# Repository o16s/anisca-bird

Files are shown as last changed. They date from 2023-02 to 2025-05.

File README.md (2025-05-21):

# Anisca Bird

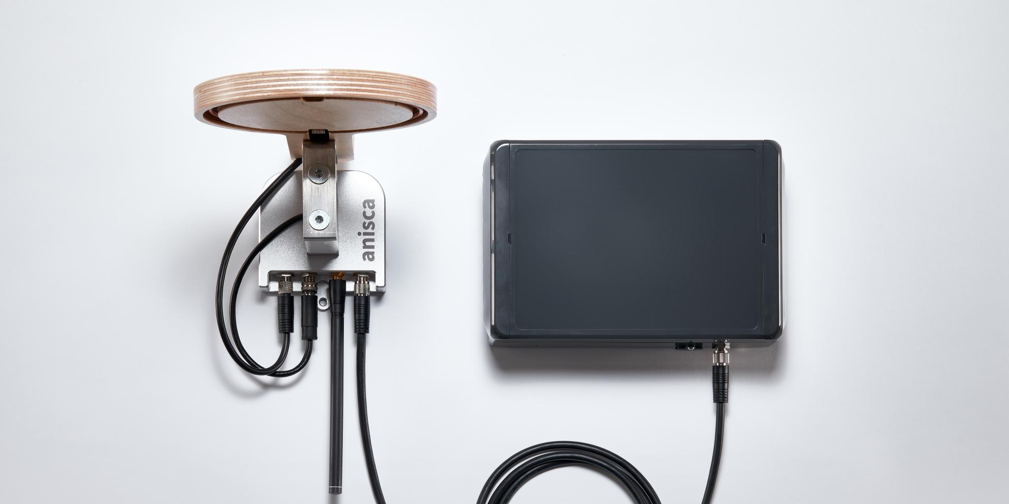
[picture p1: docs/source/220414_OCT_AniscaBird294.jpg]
Anisca Bird


## Overview

Anisca Bird is a smart weighing and tracking device developed by Octanis Instruments in collaboration with the Swiss Ornithological Institute. The system replaces a bird's regular roosting place with a weighing and tracking device that can register a bird's identity and body weight throughout the year without causing stress to the animal.

This repository contains the firmware, PCB design files, and mechanical designs to build and operate the Anisca Bird system.

## Key Features

- **RFID Identification**: Automatically reads passive RFID tags attached to birds
- **Weight Measurement**: Precision load cell with 1g resolution when calibrated
- **Data Storage**: Onboard memory for up to 18 years of weight records
- **Wireless Connectivity**: Optional Sigfox connectivity for remote data transmission
- **USB Connection**: Easy data transfer via USB-C port
- **Long Battery Life**: Up to 1 year with the external battery box
- **Modular Design**: Easy to modify, repair, or upgrade

## Repository Structure

- **`/mechanical`**: Mechanical design files (STEP format)
- **`/nestbox-electronics-master`**: PCB design files for the main board, RFID antenna, and battery box
  - **`/LF_Antenna_v3`**: RFID antenna PCB design
  - **`/Nestbox_v3_3*`**: Main board iterations
  - **`/battery_box`**: Battery box PCB design
  - **`/lib_fp.pretty`**: KiCad footprint libraries
  - **`/lib_sch`**: KiCad schematic libraries
- **`/nestbox-firmware-REV3.3`**: Firmware source code
  - **`/nestbox-fw`**: Core firmware files
  - **`/Core`**: Main application code
  - **`/Drivers`**: Hardware driver files
  - **`/Middlewares`**: Middleware components
  - **`/USB_DEVICE`**: USB communication stack

## Hardware Overview

The Anisca Bird system consists of three main components:

1. **Reader**: Contains the main PCB with microcontroller, load cell interface, RFID reader, flash memory, and connectivity options. Housed in a water-resistant aluminum case.

2. **Perch**: Varnished plywood perch with integrated 125kHz RFID antenna for tag reading with up to 10cm range.

3. **Battery Box**: External battery case with four 10Ah NiMH D-cells providing up to 1 year of operation.

## Firmware Overview

The firmware is built for STM32L433 microcontroller and provides the following functionality:

- RFID tag detection and decoding
- Weight measurement and analysis
- Low-power operation for extended battery life
- USB communication for data retrieval and configuration
- Optional Sigfox connectivity for remote data transmission

## License

Where not otherwise specified, the [GPL License](LICENSE) applies.

## Contact

For commercial support or to request an Anisca Bird system, please contact:

Octanis Instruments GmbH  
Europa-Strasse 33, 8152 Glattbrugg, Switzerland  
info@octanis.ch  
www.octanis.ch

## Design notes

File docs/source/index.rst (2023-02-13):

Welcome to Anisca Bird's documentation!
===================================

Anisca Bird replaces the usual roosting place with a weighing and tracking 
device and can be used with owls, eagles, pigeons, chickens and any other bird that can be ringed.

Contents
--------

.. toctree::
   weight
   status
   webhooks

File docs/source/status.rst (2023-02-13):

Device Status
===================================

While the anisca device is running, ystem status data is continuously logged and stored on the onboard memory ("offline"). Some logs are also transmitted wirelessly via SIGFOX ("uplink" - if coverage is available).

Logging frequency:

* offline: every 3 minutes
* uplink: 3x per day

For more details on the logged data fields see: :ref:`Status <Status Message>`.

Battery Voltage
--------

The battery voltage is measured directly on the mainboard using a resistive divider and an onboard ADC. The reference voltage is VCC, generated from the 3.3V buck converter.

The ADC value is scaled in order to indicate the battery voltage in mV.

Limits and Thresholds
~~~~~~~~~~~~~~~~~~~~~~~~~~~~~~
Rechargeable NiMH batteries should not be discharged below 0.9V per cell. Depending on the measured battery voltage, the device may decide to go to deep-sleep mode in order to protect the batteries.

Below are the hard-coded voltage values that are used to characterize the batteries' charging state. Note that 4x NiMH are powering the system (nominal 4 x 1.2 V)

* VBAT_FULL: 5350 mV. 
  Batteries are considered to be 100% charged
* VBAT_EMPTY: 3600 mV. 
  Batteries are considered to be 0% charged
* VBAT_SHUTDOWN: 3800 mV. When below this voltage, the system will go to deep sleep and weight logging and message transmission is disabled.
* VBAT_STARTUP_MIN: 4200 mV. At boot, the battery voltage must be at least this value in order for the device to complete start-up, else it will go directly to deep sleep. This means, the inserted batteries must be charged to at least this value.

Uptime 
--------
Number of days since last reboot. A reboot happens when the batteries get replaced and upon an unexpected error. If the number of days displayed in the uptime field is smaller than the number of days since the last battery replacement, an unexpected error may have occured. Please service the device if this is observed multiple times. 

Memory usage
--------
The onboard-memory can store up to 3 million log messages. The memory usage is reported as percentage (100 = memory full). The memory can be erased using the anisca App. 

Clock difference
--------
The on-board clock may drift by several seconds per day. If the device has SIGFOX connectivity and the clock difference is too high, a clock update is performed once per day. The clock can also be updated by connecting to the device via USB and using the anisca App.

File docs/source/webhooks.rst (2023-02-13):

Webhooks
===================================

The primary method that Anisca Bird uses to deliver data is through the use of webhooks.
A webhook URL will be called via a POST request with the message encoded as a JSON body. 

Messages
--------

Your webhook URL should be prepared to receive the following messages:

``weight``: Bird detected and weighed
~~~~~~~~~~~~~~~~~~~~~~~~~~~~~~~~~~~~~
.. _Weight Message:

This message is sent when a ringed bird is detected on the perch. A detection is valid if the RFID tag was successful read.

.. http:post:: example.com/webhook

    **Example request body**:

    .. sourcecode:: json

        {
            "timestamp": 1648642396,
            "serial": "CODEABFFEE",
            "device_id": "secret-red-wake",
            "type": "weight",

            "activation": {

                "latlng": "46.535,6.569",
                "site_id": "rdc20",
                "activation_date": 1648641394
            },

            "body": {

                "duration": 12,
                "flags":"ab",
                "weight": 120.5,
                "uid": "0600c9a463",
                "raw_adc_pos": 56020,
                "stddev": 1,
                "temperature": -10
            }
        }

    :<json integer timestamp: Epoch timestamp (UTC+0): seconds since January 1, 1970 12:00:00 AM
    :<json string serial: device serial number
    :<json string device_id: human readable hash of serial number that is also printed on device label
    :<json string type: message type (one of ``weight``, ``status``, ``offset``, or ``calibration``)
    :<json string activation: when and where this device was last activated

    :<json integer duration: number of seconds that owl is on perch (max. 240)
    :<json integer flags: reserved
    :<json integer weight: weight estimate in 0.01 grams (unsigned value)
    :<json integer uid: RFID UID (hexadecimal). Attention: the second byte of the RFID tag is not transmitted in order to save data. Example: The UID 050031b049 will become 0531b049.
    :<json integer raw_adc_pos: raw ADC value from "positive excitation" (incl. offset)
    :<json integer stddev: weight measurement series standard deviation in 0.1 grams
    :<json integer temperature: temperature in degrees Celsius (signed value)

.. _Status Message:
``status``: Device status
~~~~~~~~~~~~~~~~~~~~~~~~~~

Device status is sent twice a day.

.. http:post:: example.com/webhook

    **Example request body**:

    .. sourcecode:: json

        {
            "timestamp": 1648642396,
            "serial": "CODEABFFEE",
            "device_id": "secret-red-wake",
            "type": "status",

            "activation": {

                "latlng": "46.535,6.569",
                "site_id": "rdc20",
                "activation_date": 1648641394
            },

            "body": {

                "header": "ff",
                "events_with_id": 29,
                "events_unknown_id": 16,
                "flags": "ab",
                "vbat_mv": 4620,
                "memory_used": 56,
                "days_since_boot": 120
            }
        }

    :<json integer timestamp: Epoch timestamp (UTC+0): seconds since January 1, 1970 12:00:00 AM
    :<json string serial: device serial number
    :<json string device_id: human readable hash of serial number that is also printed on device label
    :<json string type: message type (one of ``weight``, ``status``, ``offset``, or ``calibration``)
    :<json string activation: when and where this device was last activated

    :<json integer header: internal device status header (0xFF)
    :<json integer events_with_id: number of events with successful RFID detection since last status update [0-255]. The value of 255 means >=255.
    :<json integer events_unknown_id: number of events with UN-successful RFID detection since last status update [0-255]. The value of 255 means >=255.
    :<json integer flags: reserved
    :<json integer vbat_mv: Battery voltage in mV
    :<json integer memory_used: Percentage of Flash memory used [0-100]
    :<json integer days_since_boot: Number of days since last reboot [0-255]. The value of 255 means >=255.

``offset``: Tare weight
~~~~~~~~~~~~~~~~~~~~~~~~~~

This is the tare weight (unladen weight) and is sent every 2 hours.

.. http:post:: example.com/webhook

    **Example request body**:

    .. sourcecode:: json

        {
            "timestamp": 1648642396,
            "serial": "CODEABFFEE",
            "device_id": "secret-red-wake",
            "type": "offset",
            
            "activation": {

                "latlng": "46.535,6.569",
                "site_id": "rdc20",
                "activation_date": 1648641376
            },

            "body": {

                "header": "fa",
                "flags": "ac",
                "weight": 31660,
                "raw_adc_pos": 4999,
                "raw_adc_neg": 4986,
                "stddev": 0,
                "temperature": 20
            }
        }

    :<json integer timestamp: Epoch timestamp (UTC+0): seconds since January 1, 1970 12:00:00 AM
    :<json string serial: device serial number
    :<json string device_id: human readable hash of serial number that is also printed on device label
    :<json string type: message type (one of ``weight``, ``status``, ``offset``, or ``calibration``)
    :<json string activation: when and where this device was last activated

    :<json integer header: internal device status header (0xFA)
    :<json integer flags: reserved
    :<json integer raw_adc_pos: raw tare ADC value from "positive excitation"
    :<json integer raw_adc_neg: raw tare ADC value from "negative excitation"
    :<json integer stddev: tare measurement series standard deviation in 0.1 grams
    :<json integer temperature: temperature in degrees Celsius (signed value)

``calibration``: Calibration result
~~~~~~~~~~~~~~~~~~~~~~~~~~~~~~~~~~~~~~~~~~

This message is sent after the user has performed a calibration.

.. http:post:: example.com/webhook

    **Example request body**:

    .. sourcecode:: json

        {
            "timestamp": 1648642396,
            "serial": "CODEABFFEE",
            "device_id": "secret-red-wake",
            "type": "calibration",

            "activation": {

                "latlng": "46.535,6.569",
                "site_id": "rdc20",
                "activation_date": 1648641376
            },

            "body": {

                "slope": 29,
                "intercept": 25,
                "temperature": 2,
                "r2": 1.0
            }
        }

    :<json integer timestamp: Epoch timestamp (UTC+0): seconds since January 1, 1970 12:00:00 AM
    :<json string serial: device serial number
    :<json string device_id: human readable hash of serial number that is also printed on device label
    :<json string type: message type (one of ``weight``, ``status``, ``offset``, or ``calibration``)
    :<json string activation: when and where this device was last activated

    :<json integer slope: linear regression slope: (raw ADC counts per 10mg)
    :<json integer intercept: linear regression intercept: (raw ADC value)
    :<json float r2: linear regression R^2
    :<json integer temperature: temperature in degrees Celsius (signed value)

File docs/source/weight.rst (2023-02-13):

Weight Measurement
===================================

Any bird weighing event is recorded and stored to memory as a new log entry. In addition, continuous offset measurements and calibration data are logged. The most important logs are also transmitted wirelessly via SIGFOX (if coverage is available).

Bird Weight
--------
Anisca Bird continuously measures the weigth present on the wooden perch ("Detection"). It does so in a low-power fashion until the measured weight is above WAKE_UP_THRESHOLD. The device then attempts to read the RFID tag of a potential bird present. If successful, the weight is measured continuously ("Acquisition") for as long as it stays above WAKE_UP_THRESHOLD.

Detection
~~~~~~~~~~~~~~~~~~~~~~~~~~~~~~

During detection, the following hard-coded constants are used:

* Low-power detection interval: 1 second
* WAKE_UP_THRESHOLD: 50 grams [#f1]_
* RFID read attempts: max. 10x in 3 second intervals. If unsuccessful after this, system goes back to sleep.

Acquisition
~~~~~~~~~~~~~~~~~~~~~~~~~~~~~~
After a bird was detected and a valid RFID was read out, its weight is sampled continuously. Multiple samples are taken into account 
because the bird may be moving and hence an instantaneous measurement would not provide a reliable weight value. 

The final **raw weight** value is obtained as a result of 3 acquisition steps:

1. **Sub-samples**: The load cell ADC is sampling the weight at 10 Hz. 
2. **Samples**: Always 10 sub-samples are averaged to create one sample. A standard deviation on the 10 sub-samples is calculated. 

    a. If the sub-sample standard deviation for a given group of 10 exceeds MAX_SUB_STDEV, the sample gets discarded. This ensures only samples where the bird was sitting still will be considered.
    b. If a sample is MAX_SAMPLE_DIFF larger than the previous sample, then the previous sample gets discarded. This ensures all samples to be on a relatifely flat line and removes outliers.

3. **Median**: A maximum of N_SAMPLES is collected as described in points 1 & 2. If the bird leaves before reaching N_SAMPLES, a smaller number of samples will be available.

    a. The median value over all collected samples is calculated. This is the retained **raw weight** value.
    b. The standard deviation over all collected samples is calculated. This is the retained **raw stddev** value.

Hard-coded parameters:

* MAX_SUB_STDEV: 5 grams [#f1]_
* MAX_SAMPLE_DIFF: 5 grams [#f1]_
* N_SAMPLES: 19

Processing
~~~~~~~~~~~~~~~~~~~~~~~~~~~~~~
The **raw weight** and **raw stddev** values obtained above are unitless ADC values. They need to be converted to grams using calibration data in order to present meaningful weight data. This is done as follows:

1. The last recorded **raw offset** value is subtracted from the **raw weight**, in order to receive the **net raw weight**
2. **net raw weight** and  **raw stddev** are divided by the most recently measured **calibration slope** to obtain weight and standard deviation of the sample in grams.

Logging
~~~~~~~~~~~~~~~~~~~~~~~~~~~~~~
For more details on what data is logged or transmitted, see: :ref:`Weight <Weight Message>`.

Offset measurement
--------

The **raw offset** is measured in the exact same way as the bird weight, except that it happens in a periodic manner whenever the weight detection stays below the WAKE_UP_THRESHOLD. 

The following parameters are hard-coded:

* N_OFFSET_SAMPLES: 11
* Offset acquisition & logging period: 3 minutes
* Offset uplink period (transmitted via SIGFOX): 1-2 hours

Calibration 
--------

The calibration is a linear regression between raw ADC values and the weight placed on the perch in grams. We denote the following terms:

* **Slope (a)**: the multiplication factor between grams and raw ADC value
* **Intercept (b)** the calculated raw ADC value when zero weight is placed on the perch. Theoretically, this is the offset value during calibration.
* **R^2** the R-square of the linear regression.

When performing a calibration routine, both a and b are calculated automatically by the device and stored for internal use. All subsequent weight measurements are processed using these most up-to-date calibraion values.

It is known that the calibration values can change over time as the physical state of the sytstem changes. Therefore, frequent re-calibrations of the system are advised.

Temperature Dependency
~~~~~~~~~~~~~~~~~~~~~~~~~~~~~~

It is known that notably the calibration slope is temperature dependent. This dependency is not compensated for by the device. It is adviseed to perform a temperature compensation of the logged weight values once the relationship between temperature and slope has been established in a post-processing step. 

.. rubric:: Footnotes
.. [#f1] Note: the values in grams are internally converted into raw ADC values by using the last available calibration slope.

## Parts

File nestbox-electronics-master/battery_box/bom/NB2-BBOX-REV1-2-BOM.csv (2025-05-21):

Reference | Quantity | Value | Footprint | Datasheet | MPN | MPN2
BT1 | 1 | Battery-4xNiMH | TerminalBlock_Dinkle:TerminalBlock_Dinkle_DT-55-B01X-02_P10.00mm
BZ1 | 1 | DNP | Buzzer_Beeper:Buzzer_CUI_CPT-9019S-SMT |  | SMT-0827-SW-5V-R
C1 C2 C3 | 3 | 10u | Capacitor_SMD:C_0805_2012Metric
C101 | 1 | DNP | Capacitor_SMD:C_0805_2012Metric
D1 | 1 | DNP | Diode_SMD:D_SOD-323 |  | B0520WS-7-F
D2 | 1 | schottky | Diode_SMD:D_SOD-323 |  | B0520WS-7-F
D3 | 1 | Red LED | LED_THT:LED_D5.0mm |  | WP934EW/ID
D4 | 1 | DNP | Package_TO_SOT_SMD:SOT-723 |  | SZESD7205DT5G
D5 | 1 | TVS DIODE 12V 23.7V | Diode_SMD:D_SOD-523 |  | UCLAMP1201H.TCT
G1 | 1 | LOGO | lib_fp_global:oi_logo_small
H1 H3 H5 H7 | 4 | MountingHole_Pad | MountingHole:MountingHole_4.5mm
H2 H4 H6 H8 | 4 | MountingHole_Pad | MountingHole:MountingHole_3.5mm
J1 J3 | 2 | FC-M8-5 | lib_fp:M8-5 | http://www.mouser.com/ds/2/18/40_c091_abd_e-75918.pdf | MB08MBSBFF05RA | 1424240
J2 | 1 | USB_C_Receptacle_USB2.0 | lib_fp:USB_C_Receptacle_HRO_TYPE-C-31-M-12 | https://www.jae.com/en/releases/detail/id=92529 | USB4105-GF-A
LOGO1 | 1 | Logo_Open_Hardware_Small | lib_fp:VogelwarteLogo3
LS1 | 1 | SMT-0931-S-R | lib_fp:SMT-0931-S-R |  | SMT-0931-S-R
Q1 | 1 | NMOS 30V 4A | Package_TO_SOT_SMD:SOT-23 |  | PMV45EN2R
Q2 | 1 | PMOS 20V 3A | Package_TO_SOT_SMD:SOT-23 |  | DMP2160U-7
R1 | 1 | 1k | Resistor_SMD:R_0603_1608Metric
R2 | 1 | 430R | Resistor_SMD:R_0603_1608Metric
R3 R5 | 2 | 0R | Resistor_SMD:R_0603_1608Metric
R4 R6 R7 R8 | 4 | 5k1 | Resistor_SMD:R_0603_1608Metric
R10 R101 R9 | 3 | DNP | Resistor_SMD:R_0603_1608Metric

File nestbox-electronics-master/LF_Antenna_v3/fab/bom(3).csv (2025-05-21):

Row | Description | Part | References | Value | Footprint | Quantity Per PCB | Datasheet | MPN
1 |  | CONSMA003.031-G | J1 | SMA-Female | LINX_CONSMA003.031-G | 1 |  | CONSMA003.031
2 | Inductor | L | L1 | LF-ANT | R_1206_3216Metric | 1 | ~ | OCTANIS-JZCOIL-120
Project info:
Schematic: | LF_Antenna_v3
Variant: | default
Revision:
Date: | 2021-03-15_15-58-28
KiCad Version: | 5.1.6-c6e7f7d~87~ubuntu20.04.1
Statistics:
Component Groups: | 2
Component Count: | 2
Fitted Components: | 2
Number of PCBs: | 1
Total Components: | 2

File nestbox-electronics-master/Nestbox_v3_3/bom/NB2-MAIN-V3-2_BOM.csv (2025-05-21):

Reference | Quantity | Value | Footprint | Datasheet | MPN | MPN2 | Description | Height | MPN-adj
BT1 | 1 | Battery-RESCUE-Nestbox_v1 | Battery:BatteryHolder_MPD_BC2003_1x2032 |  | BAT-HLD-002-SMT
C101 C201 C203 C208 C209 C210 C401 C501 C503 | 9 | 10u | Capacitor_SMD:C_0805_2012Metric
C205 | 1 | 330p | Capacitor_SMD:C_0603_1608Metric
C207 | 1 | 33p | Capacitor_SMD:C_0603_1608Metric
C206 C301 C302 | 3 | 12p | Capacitor_SMD:C_0603_1608Metric
C303 C304 | 2 | 22p | Capacitor_SMD:C_0603_1608Metric
C202 C204 C305 C311 C312 C608 | 6 | 1u | Capacitor_SMD:C_0603_1608Metric
C306 C307 C308 C313 C502 C504 C507 C508 C606 C609 C611 | 11 | 100n | Capacitor_SMD:C_0603_1608Metric
C310 C505 C506 C509 | 4 | 10n | Capacitor_SMD:C_0603_1608Metric
CRES502 CRES503 | 2 | 1n5 450V C0G | Capacitor_SMD:C_0805_2012Metric |  | CGA4F4C0G2W152J085AE
Cdiv501 | 1 | 10p 500V | Capacitor_SMD:C_0805_2012Metric |  | C0805C100JDGACTU
Cdiv502 | 1 | 1n | Capacitor_SMD:C_0603_1608Metric
D101 D302 | 2 | ESD7205 | Package_TO_SOT_SMD:SOT-723 |  | SZESD7205DT5G
D201 | 1 | TVS DIODE 12V 23.7V | Diode_SMD:D_0402_1005Metric |  | ESD9X12ST5G
D303 | 1 | LED_YELLOW | LED_SMD:LED_0603_1608Metric
J101 | 1 | FC-M8-5 | lib_fp:M8-5 | http://www.mouser.com/ds/2/18/40_c091_abd_e-75918.pdf | MB08MBSBFF05RA | 1424240
J401 J402 | 2 | Conn_01x10_Female | Connector_PinSocket_2.00mm:PinSocket_1x10_P2.00mm_Vertical_SMD_Pin1Right |  | NPPN101BFLC-RC
J1 J601 | 2 | LOAD_CELL_CONN_01X04 | lib_fp:MB08MBSAFF04RA |  | MB08MBSAFF04RA | M8S-04PMMR-SF8001
L201 | 1 | 5uH | Inductor_SMD:L_Taiyo-Yuden_NR-60xx_HandSoldering |  | MSS7341-502NLD
L202 | 1 | 4.7uH | Inductor_SMD:L_1008_2520Metric |  | DFE252010P-4R7M=P2
L301 | 1 | 10u | Inductor_SMD:L_0402_1005Metric |  | MPZ1005S300CT000
Q201 | 1 | TPH1R712MDL1Q | lib_fp:TDSON-8-1_HandSoldering |  | TPH1R712MD,L1Q
Q301 Q601 Q603 | 3 | PMOS 20V 3A | Package_TO_SOT_SMD:SOT-23 |  | DMP2160U-7
Q501 Q602 Q604 | 3 | NMOS 30V 4A | Package_TO_SOT_SMD:SOT-23 |  | PMV45EN2R
R101 R102 R303 R307 R605 R615 R616 R617 | 8 | 47R | Resistor_SMD:R_0603_1608Metric
R202 R203 R207 | 3 | 162k 0.1% | Resistor_SMD:R_0603_1608Metric
R206 | 1 | 15k | Resistor_SMD:R_0603_1608Metric
R208 | 1 | 649k 1% | Resistor_SMD:R_0603_1608Metric
R306 | 1 | 1k | Resistor_SMD:R_0603_1608Metric
R205 R401 | 2 | 10k | Resistor_SMD:R_0603_1608Metric
R201 R302 R304 R403 R504 R601 R602 R603 R604 | 9 | 100k | Resistor_SMD:R_0603_1608Metric
R501 R607 R608 R611 R612 R614 R618 CRES501 | 8 | 0R | Resistor_SMD:R_0603_1608Metric
U201 | 1 | TPS62745 | lib_fp:WSON_3x2mm_12pin |  | TPS62745DSSR
U202 | 1 | LTC3534 | Package_SO:SSOP-16_3.9x4.9mm_P0.635mm |  | LTC3534EGN#PBF
U203 | 1 | 3.0V LDO | Package_TO_SOT_SMD:SOT-23-5 |  | TPS70630DBVR | TPS7A20 |  |  | TPS76201QDBVRQ1
U301 | 1 | STM32L433CCxx | Package_DFN_QFN:QFN-48-1EP_7x7mm_P0.5mm_EP5.3x5.3mm | http://www.st.com/st-web-ui/static/active/en/resource/technical/document/datasheet/DM00257192.pdf | STM32L433CCU6
U302 | 1 | 1Gb NAND Flash | lib_fp:8-LGA-6x8mm |  | GD5F1GQ4UFYIGR
U401 | 1 | Power Switch 2A, 800us soft start | lib_fp:IC_MIC94085YFT-TR |  | MIC94082YFT-TR
U501 | 1 | EM4095 | Package_SO:SOIC-16_3.9x9.9mm_P1.27mm |  | EM4095
U601 | 1 | ADS1220 | Package_SO:TSSOP-16_4.4x5mm_P0.65mm |  | ADS1220IPW
U602 | 1 | DNP | Oscillator:Oscillator_SMD_EuroQuartz_XO32-4Pin_3.2x2.5mm | https://abracon.com/Oscillators/ASDMB.pdf | SIT1602BI-21-XXS-4.096000
Y301 | 1 | 16MHz 10ppm 9pF | lib_fp:Crystal_SMD_2016-4Pin_2.0x1.6mm |  | ECS-160-9-37-CKM-TR |  | 16MHz ±10ppm Crystal 9pF 100 Ohms 4-SMD, No Lead | 0.6
Y302 | 1 | 32kHz 20ppm 12.5pF | lib_fp:Crystal_SMD_MicroCrystal_CC7V-T1A-2Pin_3.2x1.5mm |  | CM7V-T1A-32.768kHz-12.5pF-20PPM-TB-QC

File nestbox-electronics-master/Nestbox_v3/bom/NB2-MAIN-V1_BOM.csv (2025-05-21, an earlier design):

Reference | Quantity | Value | Footprint | Datasheet | MPN | MPN-adj | MPN2 | Description | Height
C101 C201 C203 C208 C209 C210 C401 C501 C503 C610 | 10 | 10u | Capacitor_SMD:C_0805_2012Metric
C202 C311 C312 C608 | 4 | 1u | Capacitor_SMD:C_0603_1608Metric
C204 | 1 | 1u or 4u7 for adjustable version | Capacitor_SMD:C_0603_1608Metric
C205 | 1 | 330p | Capacitor_SMD:C_0603_1608Metric
C206 | 1 | 10p | Capacitor_SMD:C_0603_1608Metric
C207 | 1 | 33p | Capacitor_SMD:C_0603_1608Metric
C301 C302 | 2 | 12p | Capacitor_SMD:C_0603_1608Metric | ~
C303 C304 | 2 | 22p | Capacitor_SMD:C_0603_1608Metric | ~
C305 | 1 | 4u7 | Capacitor_SMD:C_0603_1608Metric | ~
C306 C307 C308 C313 C502 C504 C507 C606 C609 | 9 | 100n | Capacitor_SMD:C_0603_1608Metric | ~
C310 C505 C506 C611 | 4 | 10n | Capacitor_SMD:C_0603_1608Metric | ~
C508 | 1 | DNP or 100n | Capacitor_SMD:C_0603_1608Metric | DNP
C602 | 1 | 1u DNP | Capacitor_SMD:C_0603_1608Metric
C601 C603 C604 | 3 | 100n 1% DNP | Capacitor_SMD:C_0603_1608Metric
C605 C607 | 2 | 100n DNP | Capacitor_SMD:C_0603_1608Metric
CRES501 | 1 | 0R | Capacitor_SMD:C_0603_1608Metric
CRES502 CRES503 | 2 | 1n5 450V C0G | Capacitor_SMD:C_0805_2012Metric |  | CGA4F4C0G2W152J085AE
Cdiv501 | 1 | 10p 500V | Capacitor_SMD:C_0805_2012Metric |  | C0805C100JDGACTU
Cdiv502 | 1 | 1n | Capacitor_SMD:C_0603_1608Metric
D101 D302 | 2 | ESD7205 | Package_TO_SOT_SMD:SOT-723 |  | SZESD7205DT5G
D301 | 1 | TVS DIODE 12V 23.7V | Diode_SMD:D_0402_1005Metric | ~ | ESD9X12ST5G
D303 | 1 | LED_YELLOW | LED_SMD:LED_0603_1608Metric
G101 | 1 | LOGO | lib-fp-global:oi_logo_small
H101 H102 H103 | 3 | MountingHole_Pad | MountingHole:MountingHole_3.2mm_M3_Pad_Via | ~
J101 | 1 | FC-M8-5 | Connector_Molex:Molex_PicoBlade_53398-0571_1x05-1MP_P1.25mm_Vertical | http://www.mouser.com/ds/2/18/40_c091_abd_e-75918.pdf | 53398-0571
J102 | 1 | Chassis Pin | lib_fp:SMD_PAD | ~
J301 | 1 | USB_B_Micro | Connector_USB:USB_Micro-B_Molex-105017-0001 | ~
J401 J402 | 2 | Conn_01x10_Female | Connector_PinSocket_2.00mm:PinSocket_1x10_P2.00mm_Vertical_SMD_Pin1Left | ~ | 1-2307813-0
J501 | 1 | Conn_RFID_UFL_ALT | Connector_Coaxial:U.FL_Hirose_U.FL-R-SMT-1_Vertical | ~ | U.FL-R-SMT(10)
J502 | 1 | Conn_RFID_SMA | lib_fp:SMA_Molex_EdgeMount | ~ | 0732512120
J601 | 1 | LOAD_CELL_CONN_01X04 | lib_fp:MB08MBSAFF04RA |  | M8S-04PMMR-SF8001 |  | MB08MBSAFF04RA
J602 | 1 | LOAD_CELL_CONN_01X04 | Connector_Molex:Molex_PicoBlade_53398-0471_1x04-1MP_P1.25mm_Vertical |  | 53398-0471
JP201 | 1 | Jumper_3_Bridged12 | Connector_PinHeader_2.54mm:PinHeader_1x03_P2.54mm_Vertical | ~
JP202 | 1 | 5V boost supply jumper | Connector_PinHeader_2.54mm:PinHeader_1x02_P2.54mm_Vertical | ~
JP203 | 1 | vsel 0.2 | Jumper:SolderJumper-3_P1.3mm_Bridged12_RoundedPad1.0x1.5mm | ~
JP204 | 1 | VAA jumper | Connector_PinHeader_2.54mm:PinHeader_1x02_P2.54mm_Vertical | ~
JP205 | 1 | vsel 0.1 | Jumper:SolderJumper-3_P1.3mm_Bridged12_RoundedPad1.0x1.5mm | ~
JP206 JP301 | 2 | Jumper_NC_Small | Connector_PinHeader_2.54mm:PinHeader_1x02_P2.54mm_Vertical | ~
L201 | 1 | 5uH | Inductor_SMD:L_Taiyo-Yuden_NR-60xx_HandSoldering |  | MSS7341-502NLD
L202 | 1 | 4.7uH | Inductor_SMD:L_1008_2520Metric |  | DFE252010P-4R7M=P2
L301 | 1 | 10u | Inductor_SMD:L_0402_1005Metric | ~ | MPZ1005S300CT000
LOGO101 | 1 | Logo_Open_Hardware_Small | lib_fp:VogelwarteLogo3 | ~
P301 | 1 | TC2030-MCP | lib-fp-global:TC2030-MCP-NL
Q201 | 1 | TPH1R712MDL1Q | lib_fp:TDSON-8-1_HandSoldering |  | TPH1R712MD,L1Q
Q301 Q601 Q603 | 3 | DMG2301L-7 | Package_TO_SOT_SMD:SOT-23 |  | DMG2301L-7
Q501 Q602 Q604 | 3 | NMOS 30V 4A | Package_TO_SOT_SMD:SOT-23 |  | SI2316DS-T1-E3
R101 R102 R103 R104 R205 R401 R403 | 7 | 10k | Resistor_SMD:R_0603_1608Metric | ~
R105 R106 R204 R209 R210 R301 R402 R404 R405 R503 R505 R506 R509 R613 R614 | 15 | DNP | Resistor_SMD:R_0603_1608Metric | ~
R201 R202 R302 R304 R504 R601 R602 R603 R604 | 9 | 82k | Resistor_SMD:R_0603_1608Metric
R203 | 1 | 47k | Resistor_SMD:R_0603_1608Metric
R206 | 1 | 15k | Resistor_SMD:R_0603_1608Metric
R207 | 1 | 162k 1% | Resistor_SMD:R_0603_1608Metric |  | RC0402FR-07162KL
R208 | 1 | 649k 1% | Resistor_SMD:R_0603_1608Metric |  | RC0402FR-07649KL
R303 | 1 | 100R | Resistor_SMD:R_0603_1608Metric | ~
R305 | 1 | 1k5 | Resistor_SMD:R_0603_1608Metric | ~
R306 | 1 | 1k | Resistor_SMD:R_0603_1608Metric
R501 R502 R507 R508 R605 R606 R607 R608 R609 R610 R611 R612 R618 | 13 | 0R | Resistor_SMD:R_0603_1608Metric
R615 R616 R617 | 3 | 47R | Resistor_SMD:R_0603_1608Metric
U201 | 1 | TPS62745 | lib_fp:WSON_3x2mm_12pin |  | TPS62745DSSR
U202 | 1 | LTC3534 | Package_SO:SSOP-16_3.9x4.9mm_P0.635mm |  | LTC3534EDHC#PBF
U203 | 1 | 3.0V LDO | Package_TO_SOT_SMD:SOT-23-5 |  | TPS70630DBVR | TPS76201QDBVRQ1 | TPS7A20
U301 | 1 | STM32L433CCxx | Package_DFN_QFN:QFN-48-1EP_7x7mm_P0.5mm_EP5.3x5.3mm | http://www.st.com/st-web-ui/static/active/en/resource/technical/document/datasheet/DM00257192.pdf | STM32L433CCU6
U302 | 1 | 1Gb NAND Flash | lib_fp:8-LGA-6x8mm |  | GD5F1GQ4UFYIGR
U401 | 1 | Power Switch 2A, 800us soft start | lib_fp:IC_MIC94085YFT-TR |  | MIC94082YFT-TR
U402 | 1 | XBEE | lib_fp:XBEE |  | SuperBx
U501 | 1 | EM4095 | Package_SO:SOIC-16_3.9x9.9mm_P1.27mm |  | EM4095
U601 | 1 | ADS1220 | Package_SO:TSSOP-16_4.4x5mm_P0.65mm |  | ADS1220IPW
U602 | 1 | SIT1602BI 4.096 MHz | Oscillator:Oscillator_SMD_EuroQuartz_XO32-4Pin_3.2x2.5mm | https://abracon.com/Oscillators/ASDMB.pdf | SIT1602BI-21-XXE-4.096000
Y301 | 1 | 16MHz 10ppm 9pF | lib_fp:Crystal_SMD_2016-4Pin_2.0x1.6mm |  | ECS-160-9-37-CKM-TR |  |  | 16MHz ±10ppm Crystal 9pF 100 Ohms 4-SMD, No Lead | 0.6
Y302 | 1 | 32kHz 20ppm 12.5pF | lib_fp:Crystal_SMD_MicroCrystal_CC7V-T1A-2Pin_3.2x1.5mm | ~ | CM7V-T1A-32.768kHz-12.5pF-20PPM-TB-QC

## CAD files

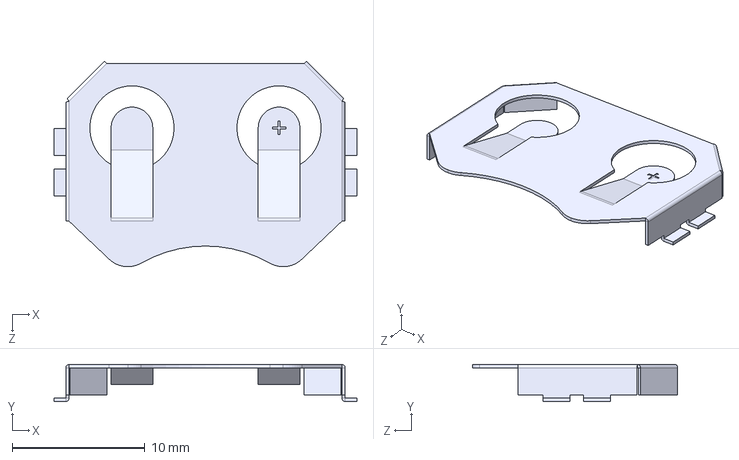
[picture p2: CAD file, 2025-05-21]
nestbox-electronics-master/3d-models/BAT-HLD-002-SMT.STEP
22.9 x 2.79 x 15.5 mm

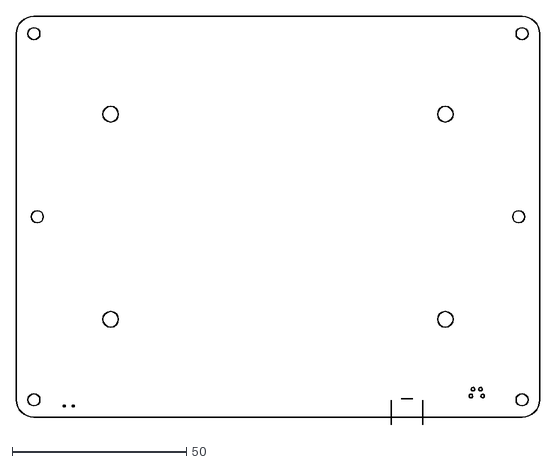
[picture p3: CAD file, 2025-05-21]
nestbox-electronics-master/battery_box/fab/cutouts_battery_box_silvester.dxf
150.0 x 117.1

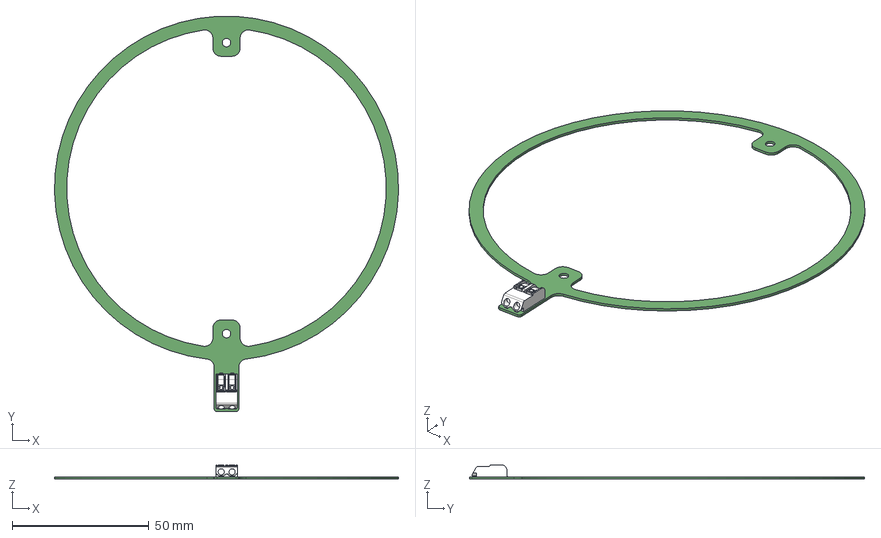
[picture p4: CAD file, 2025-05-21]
nestbox-electronics-master/LF_Antenna_v3/LF_Antenna_v3.step
126.0 x 144.7 x 5.20 mm

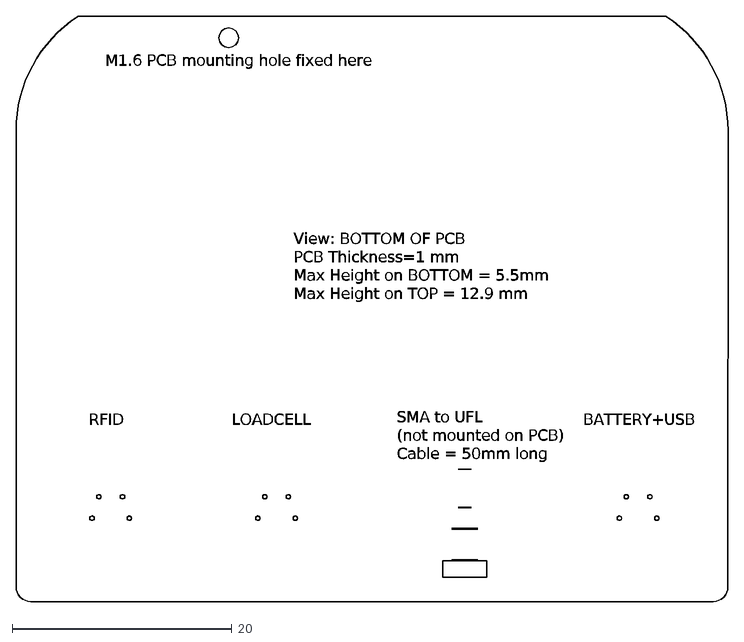
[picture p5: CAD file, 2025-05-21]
nestbox-electronics-master/Nestbox_v3_3/fab/SILVESTER_PCB_CUTOUTS.dxf
SMA to UFL (not mounted on PCB) Cable = 50mm long
LOADCELL
View: BOTTOM OF PCB PCB Thickness=1 mm Max Height on BOTTOM = 5.5mm Max Height on TOP = 12.9 mm
RFID
BATTERY+USB
M1.6 PCB mounting hole fixed here

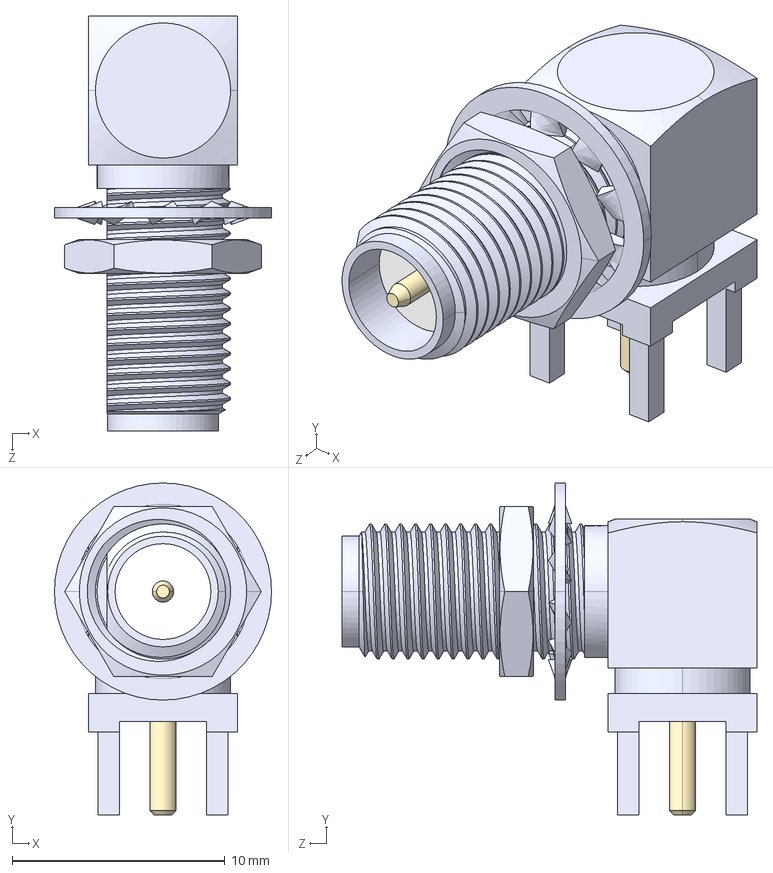
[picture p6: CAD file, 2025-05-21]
nestbox-electronics-master/3d-models/CONREVSMA002-L.step
10.2 x 15.6 x 19.5 mm
CONREVSMA002-L
Nut
Washer

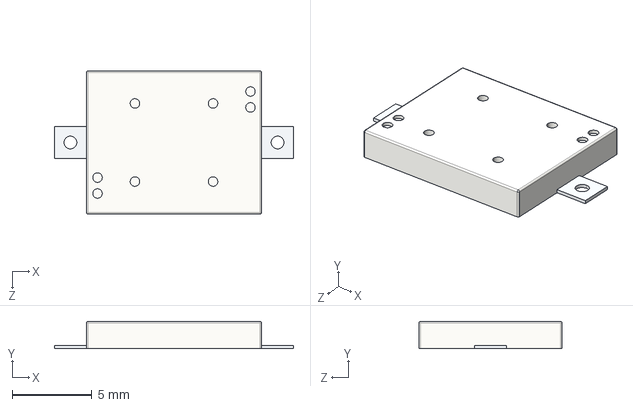
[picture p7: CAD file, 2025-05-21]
nestbox-electronics-master/3d-models/CUI_DEVICES_CPT-1117-83-SMT-TR.step
15.0 x 1.70 x 9.00 mm

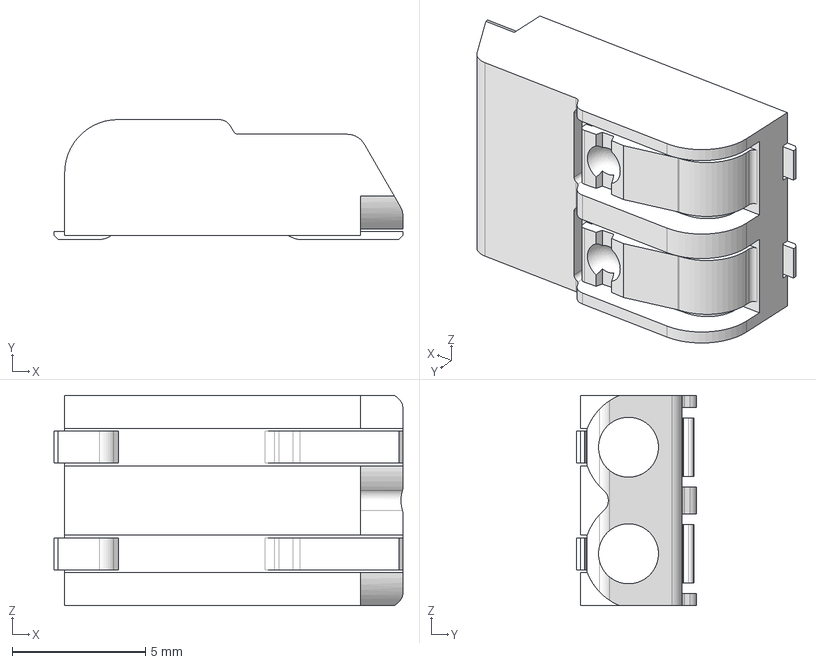
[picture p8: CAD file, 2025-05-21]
nestbox-electronics-master/3d-models/2060.step
13.1 x 4.50 x 7.90 mm

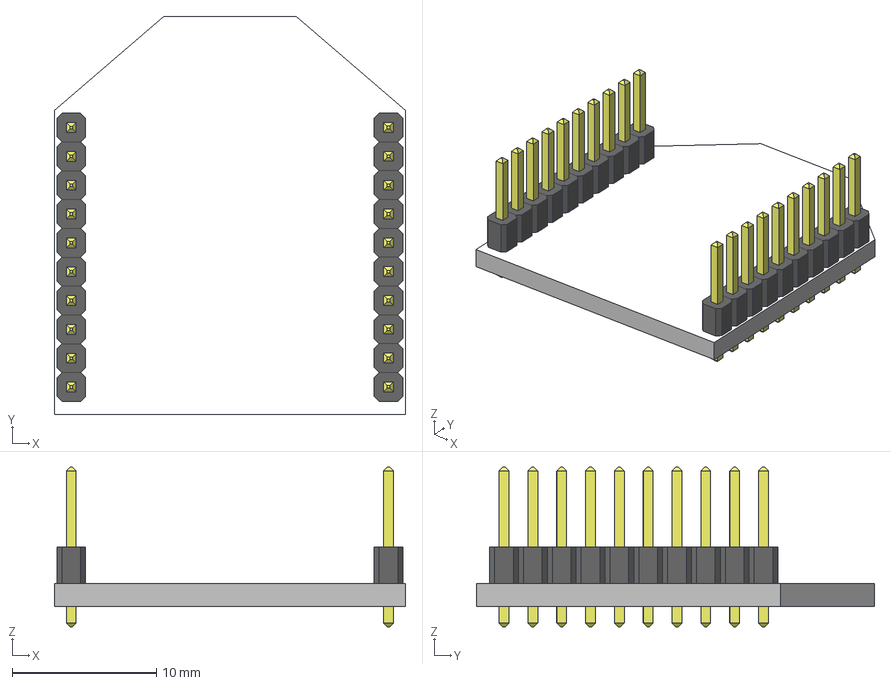
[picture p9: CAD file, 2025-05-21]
nestbox-electronics-master/3d-models/XBee.stp
24.4 x 27.6 x 11.1 mm
XBee Module - ZB Series S2C - 2mW with Wire Antenna - XB24CZ7WIT-004
2mm Header_10 x 2

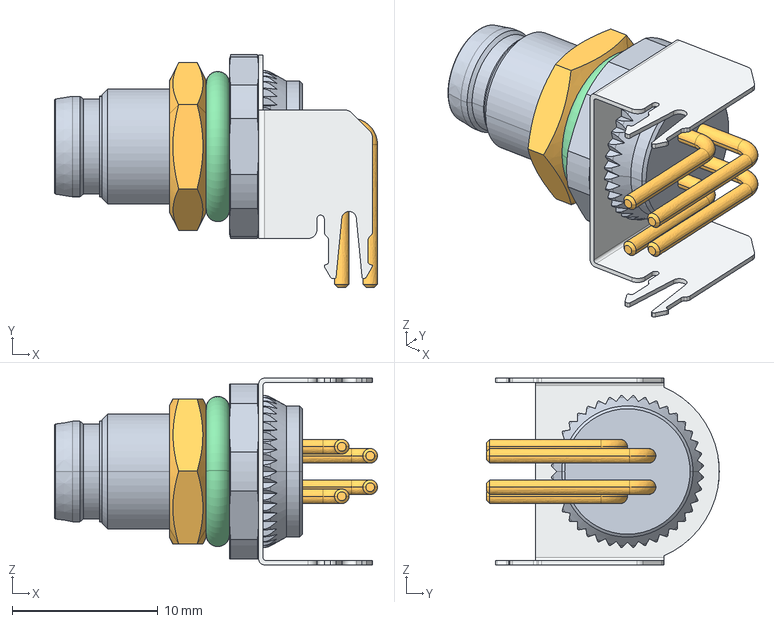
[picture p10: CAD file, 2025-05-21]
nestbox-electronics-master/3d-models/M8AS-04PMMR-SF8001-STP.stp
22.1 x 16.0 x 12.8 mm

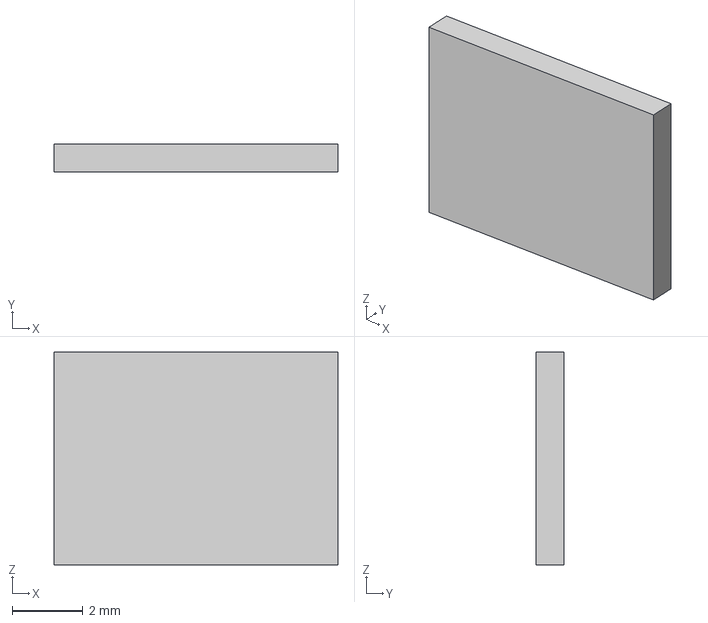
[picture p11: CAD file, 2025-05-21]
nestbox-electronics-master/3d-models/USON8-8x6mm.step
8.00 x 0.8 x 6.00 mm

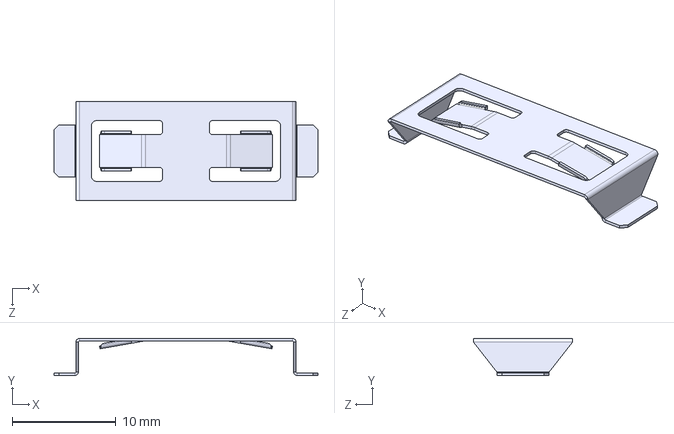
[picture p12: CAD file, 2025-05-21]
nestbox-electronics-master/3d-models/BC-2003--3DModel-STEP-1.STEP
25.4 x 3.56 x 9.53 mm

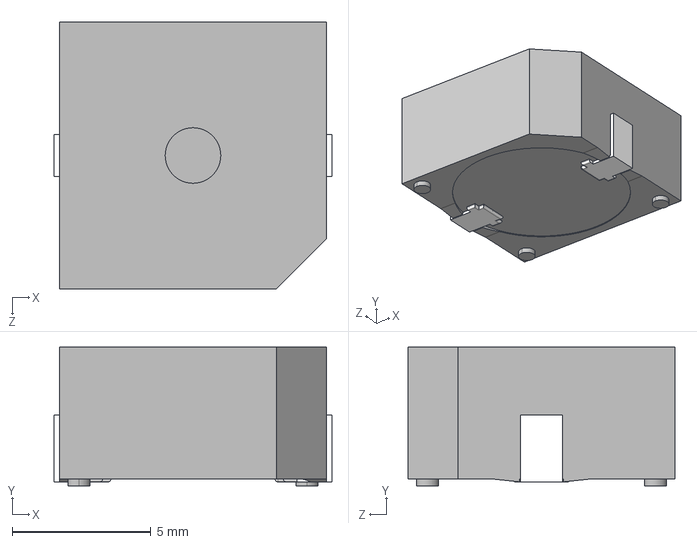
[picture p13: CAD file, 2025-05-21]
nestbox-electronics-master/3d-models/CUI_DEVICES_CMI-9655S-SMT-TR.step
10.0 x 5.00 x 9.60 mm

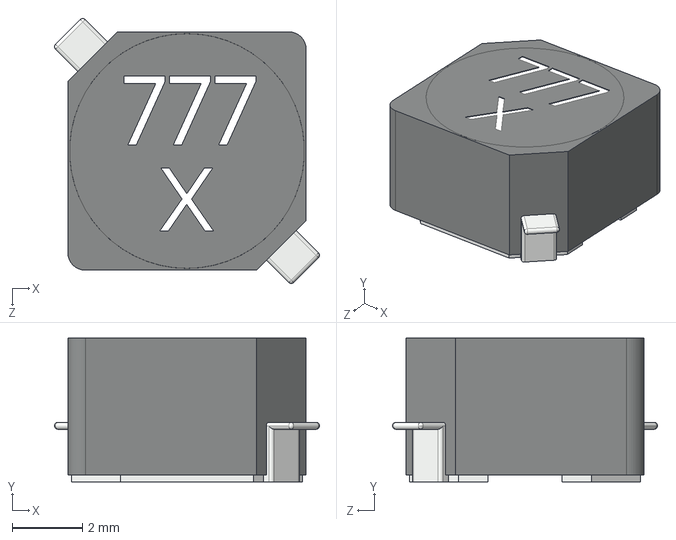
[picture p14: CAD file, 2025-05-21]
nestbox-electronics-master/3d-models/Coilcraft-MSS7341.STEP
7.56 x 4.10 x 7.56 mm

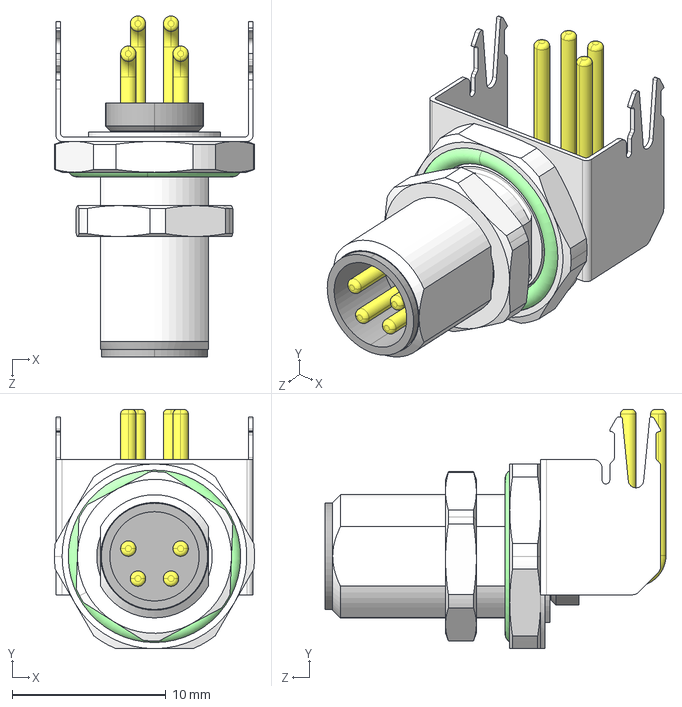
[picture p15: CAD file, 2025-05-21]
nestbox-electronics-master/3d-models/MB08MBSAFF04RA.STEP
13.0 x 15.6 x 22.1 mm

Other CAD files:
nestbox-electronics-master/3d-models/1424240.stp
nestbox-electronics-master/3d-models/732512120.stp

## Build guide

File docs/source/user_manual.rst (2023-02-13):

User Manual
===================================

TODO: calibration routine, battery change, data sync.

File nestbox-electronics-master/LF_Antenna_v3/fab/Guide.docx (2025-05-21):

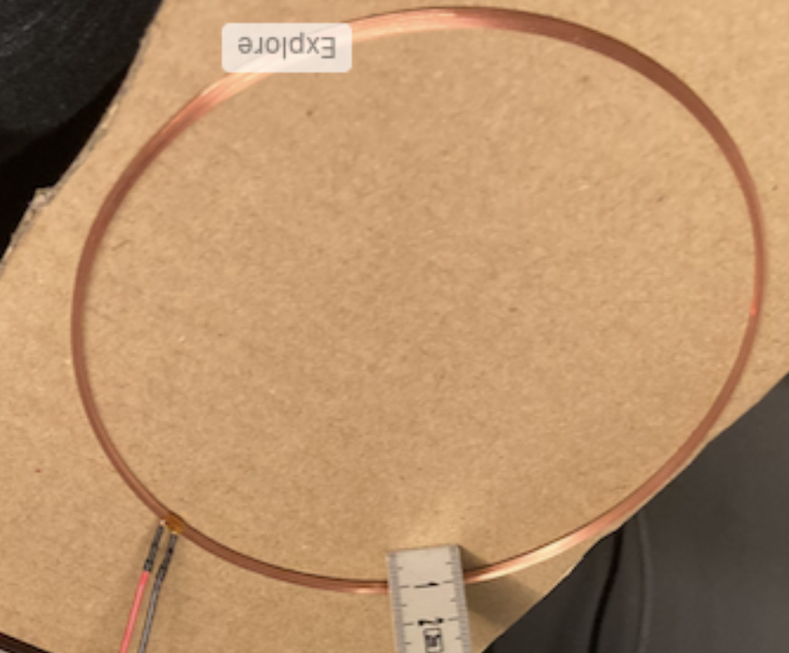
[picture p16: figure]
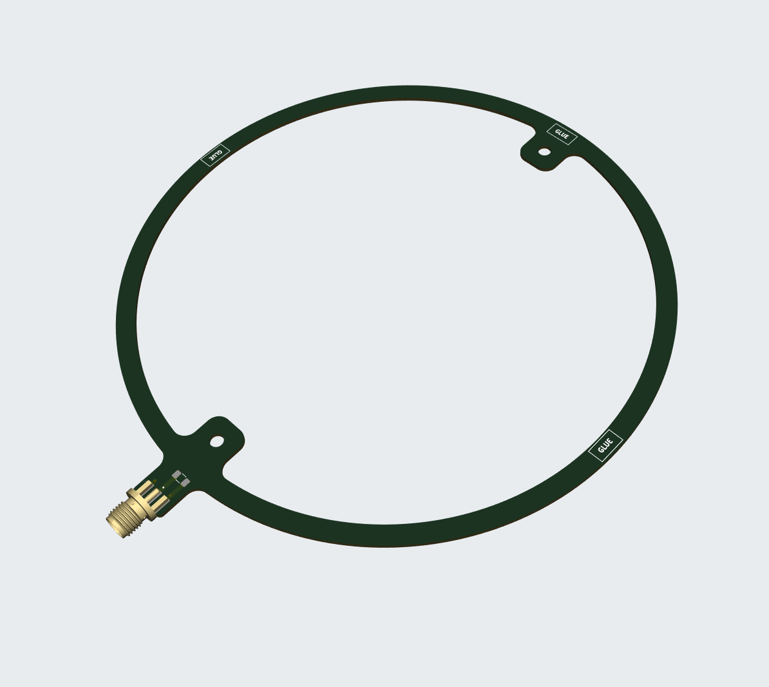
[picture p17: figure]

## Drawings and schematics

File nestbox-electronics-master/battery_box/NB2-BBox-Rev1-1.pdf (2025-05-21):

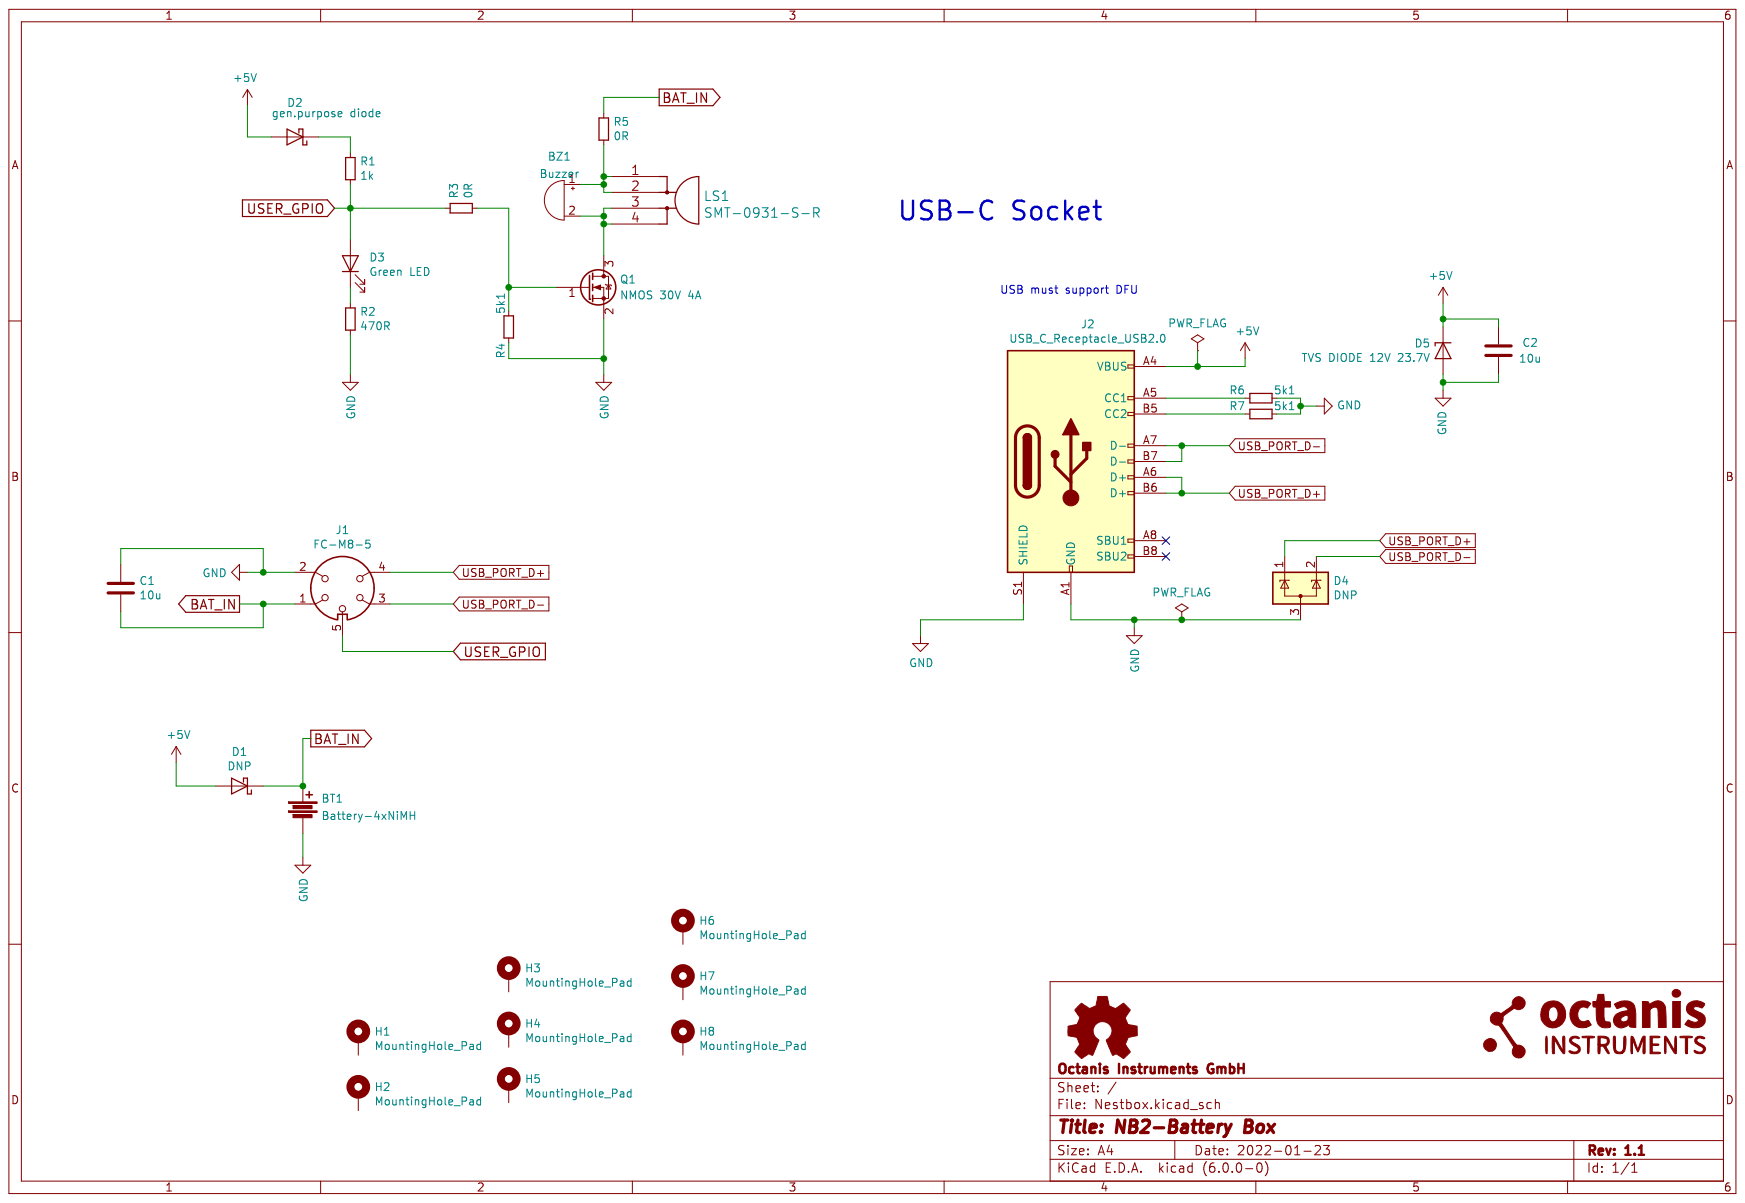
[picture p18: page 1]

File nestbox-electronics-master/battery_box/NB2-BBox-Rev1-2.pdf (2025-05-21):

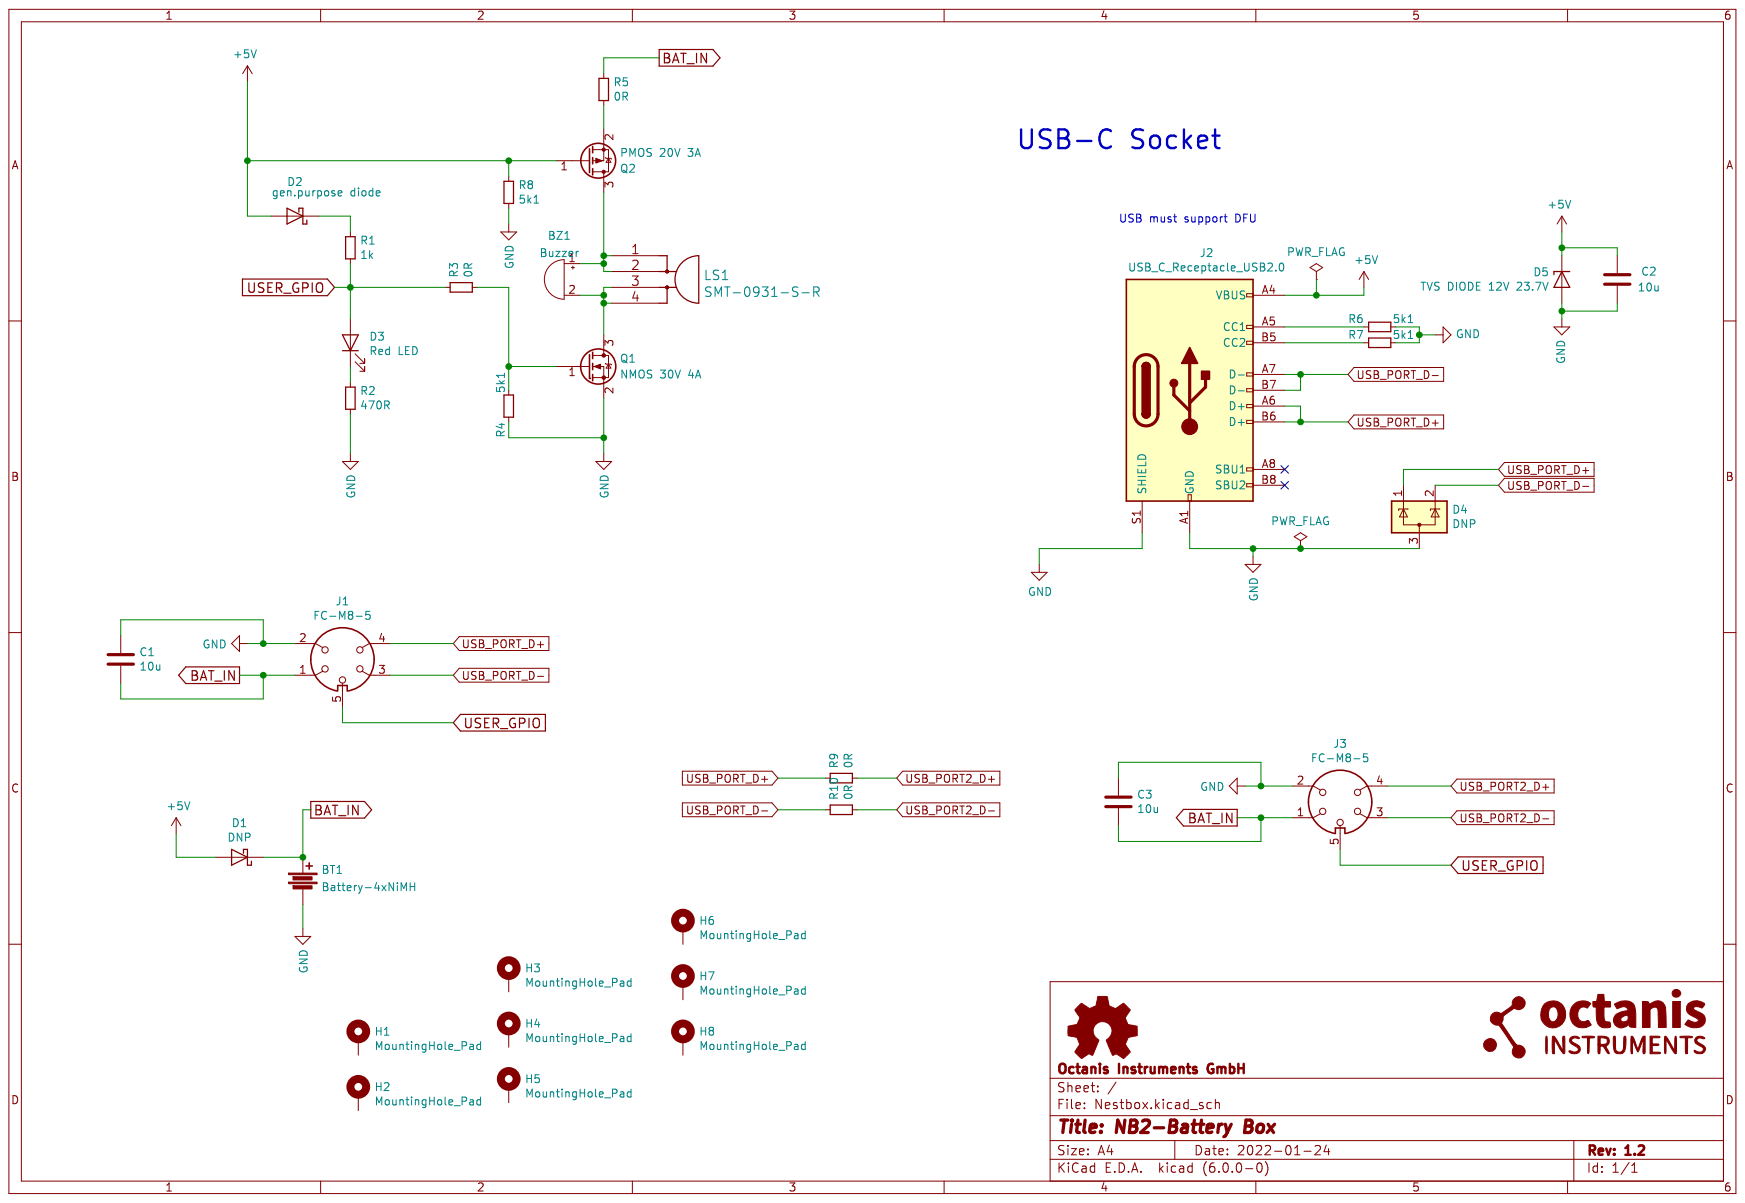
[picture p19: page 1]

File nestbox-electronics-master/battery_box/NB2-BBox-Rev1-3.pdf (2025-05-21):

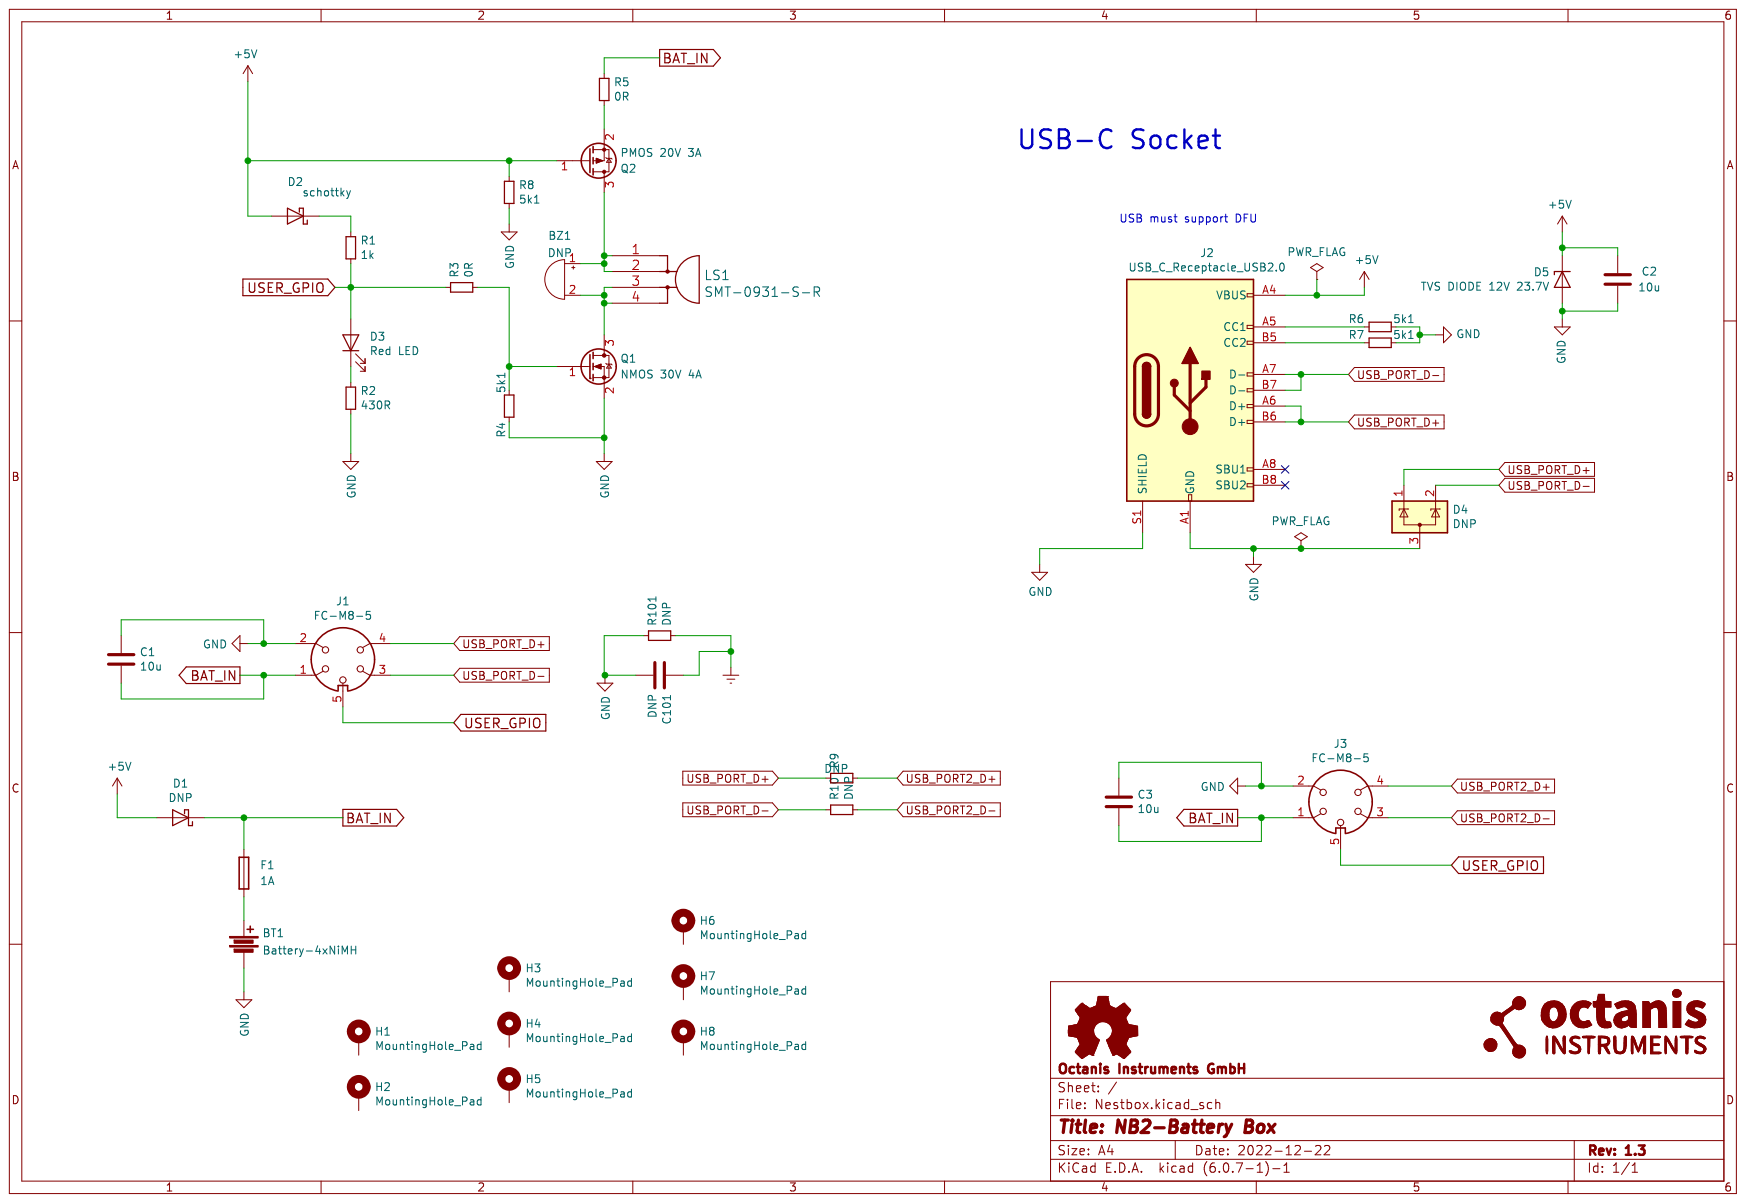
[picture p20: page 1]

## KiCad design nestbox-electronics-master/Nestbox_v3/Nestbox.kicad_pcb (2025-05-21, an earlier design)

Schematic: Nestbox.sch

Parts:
C101: 10u; C_0805_2012Metric
D101: ESD7205; SOT-723; MPN SZESD7205DT5G
G101: LOGO; oi_logo_small
H101, H102, H103: MountingHole_Pad; MountingHole_3.2mm_M3_Pad_Via
J101: FC-M8-5; Molex_PicoBlade_53398-0571_1x05-1MP_P1.25mm_Vertical; MPN 53398-0571
J102: Chassis Pin; SMD_PAD
LOGO101: Logo_Open_Hardware_Small; VogelwarteLogo3
R101, R102, R103, R104: 10k; R_0603_1608Metric
R105, R106: DNP; R_0603_1608Metric

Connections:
/ADC_CLK_EN: R106.2; also elsewhere on the board
/Communication/RF_CTS: R106.1; also elsewhere on the board
/Communication/RF_RTS: R105.1; also elsewhere on the board
/RFID_SLEEP_N: R105.2; also elsewhere on the board
BAT_IN: C101.2, J101.1; also elsewhere on the board
GND: C101.1, D101.3, J101.2, R101.2, R102.2, R103.2, R104.2; also elsewhere on the board
unnamed: H101.1, R102.1
unnamed: H102.1, R103.1
unnamed: H103.1, R104.1
unnamed: J102.1, R101.1
USB_D+: J101.4; also elsewhere on the board
USB_D-: J101.3; also elsewhere on the board
USER_GPIO: D101.2, J101.5; also elsewhere on the board

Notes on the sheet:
For first prototype, RTS and CTS are not used. GPIO’s should be re-allocated in final version!

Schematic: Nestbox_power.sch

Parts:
C201, C203, C208, C209, C210: 10u; C_0805_2012Metric
C202: 1u; C_0603_1608Metric
C204: 1u or 4u7 for adjustable version; C_0603_1608Metric
C205: 330p; C_0603_1608Metric
C206: 10p; C_0603_1608Metric
C207: 33p; C_0603_1608Metric
JP201: Jumper_3_Bridged12; PinHeader_1x03_P2.54mm_Vertical
JP202: 5V boost supply jumper; PinHeader_1x02_P2.54mm_Vertical
JP203: vsel 0.2; SolderJumper-3_P1.3mm_Bridged12_RoundedPad1.0x1.5mm
JP204: VAA jumper; PinHeader_1x02_P2.54mm_Vertical
JP205: vsel 0.1; SolderJumper-3_P1.3mm_Bridged12_RoundedPad1.0x1.5mm
JP206: Jumper_NC_Small; PinHeader_1x02_P2.54mm_Vertical
L201: 5uH; L_Taiyo-Yuden_NR-60xx_HandSoldering; MPN MSS7341-502NLD
L202: 4.7uH; L_1008_2520Metric; MPN DFE252010P-4R7M=P2
Q201: TPH1R712MDL1Q; TDSON-8-1_HandSoldering; MPN TPH1R712MD,L1Q
R201, R202: 82k; R_0603_1608Metric
R203: 47k; R_0603_1608Metric
R204, R209, R210: DNP; R_0603_1608Metric
R205: 10k; R_0603_1608Metric
R206: 15k; R_0603_1608Metric
R207: 162k 1%; R_0603_1608Metric; MPN RC0402FR-07162KL
R208: 649k 1%; R_0603_1608Metric; MPN RC0402FR-07649KL
U201: TPS62745; WSON_3x2mm_12pin; MPN TPS62745DSSR
U202: LTC3534; SSOP-16_3.9x4.9mm_P0.635mm; MPN LTC3534EDHC#PBF
U203: 3.0V LDO; SOT-23-5; MPN TPS70630DBVR

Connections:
+5V: C209.1, C210.1, JP201.3, R205.2, R208.1, U202.11 (VOUT); also elsewhere on the board
+BATT: C201.1, JP202.1, JP203.1, JP205.1, Q201.3 (S), U201.1 (VIN), U201.8 (VSEL4), U201.9 (VSEL3), U201.12 (EN)
/Control/5V_ENABLE: R201.2, U202.2 (RUN/SS); also elsewhere on the board
/Control/BAT_TEST_ENABLE: U201.4 (EN_VIN_SW); also elsewhere on the board
/Control/HK_BAT_V: R202.1, R203.2; also elsewhere on the board
/VAA_LDO_EN: R204.2, U203.3 (INH); also elsewhere on the board
BAT_IN: Q201.1 (D); also elsewhere on the board
GND: C201.2, C202.2, C203.2, C204.2, C208.2, C209.2, C210.2, JP203.3, JP205.3, Q201.2 (G), R201.1, R203.1, R204.1, R207.1, R210.1, U201.3 (GND), U201.GND1 (GND), U201.GND2 (GND), U202.1 (GND), U202.3 (GND), U202.4 (PGND1), U202.7 (PGIND2), U202.8 (GND), U202.9 (GND), U202.10 (PWM), U202.16 (GND), U203.2 (GND); also elsewhere on the board
unnamed: C202.1, JP201.2, U203.1 (VIN)
unnamed: C203.1, JP202.2, U202.12 (PVIN), U202.13 (VIN)
unnamed: C204.1, JP204.1, R209.2, U203.5 (VOUT)
unnamed: C205.1, R206.1
unnamed: C205.2, C206.2, U202.14 (VC)
unnamed: C206.1, C207.2, R206.2, R207.2, R208.2, U202.15 (FB)
unnamed: C207.1, R205.1
unnamed: C208.1, JP206.1, L202.2, U201.5 (VOUT)
unnamed: JP203.2, U201.10 (VSEL2)
unnamed: JP205.2, U201.11 (VSEL1)
unnamed: L201.1, U202.5 (SW1)
unnamed: L201.2, U202.6 (SW2)
unnamed: L202.1, U201.2 (SW)
unnamed: R202.2, U201.6 (VIN_SW)
unnamed: R209.1, R210.2, U203.4 (BYP)
VAA: JP204.2; also elsewhere on the board

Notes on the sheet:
TODO: add battery undervoltage protection circuit! (to enable pin!) Other option: Use 2 cell alkaline battery.
Low ESR capacitors should be used to minimize output voltage ripple.
2.4V to 7V VIN
InputVoltageRangeVINfrom3.3 V to 10 V
Alternative part (used in CLM proj): SSM3J338R,LF
3.0V output
Quiescent current is only 25μA in Burst Mode operation, maximizing battery life in portable applications. Burst Mode operation is user controlled and can be enabled by driving the PWM pin low.
NOTE: adjustable part has active-low ENABLE

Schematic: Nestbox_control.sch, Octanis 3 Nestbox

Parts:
C301, C302: 12p; C_0603_1608Metric
C303, C304: 22p; C_0603_1608Metric
C305: 4u7; C_0603_1608Metric
C306, C307, C308, C313: 100n; C_0603_1608Metric
C310: 10n; C_0603_1608Metric
C311, C312: 1u; C_0603_1608Metric
D301: TVS DIODE 12V 23.7V; D_0402_1005Metric; MPN ESD9X12ST5G
D302: ESD7205; SOT-723; MPN SZESD7205DT5G
D303: LED_YELLOW; LED_0603_1608Metric
J301: USB_B_Micro; USB_Micro-B_Molex-105017-0001
JP301: Jumper_NC_Small; PinHeader_1x02_P2.54mm_Vertical
L301: 10u; L_0402_1005Metric; MPN MPZ1005S300CT000
P301: TC2030-MCP; TC2030-MCP-NL
Q301: DMG2301L-7; SOT-23; MPN DMG2301L-7
R301: DNP; R_0603_1608Metric
R302, R304: 82k; R_0603_1608Metric
R303: 100R; R_0603_1608Metric
R305: 1k5; R_0603_1608Metric
R306: 1k; R_0603_1608Metric
U301: STM32L433CCxx; QFN-48-1EP_7x7mm_P0.5mm_EP5.3x5.3mm; MPN STM32L433CCU6
U302: 1Gb NAND Flash; 8-LGA-6x8mm; MPN GD5F1GQ4UFYIGR
Y301: 16MHz 10ppm 9pF; Crystal_SMD_2016-4Pin_2.0x1.6mm; MPN ECS-160-9-37-CKM-TR
Y302: 32kHz 20ppm 12.5pF; Crystal_SMD_MicroCrystal_CC7V-T1A-2Pin_3.2x1.5mm; MPN CM7V-T1A-32.768kHz-12.5pF-20PPM-TB-QC

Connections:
/ADC_CLK_EN: U301.26; also elsewhere on the board
/Communication/RF_ENABLE: U301.25; also elsewhere on the board
/Communication/RF_RX: U301.21; also elsewhere on the board
/Communication/RF_TX: U301.22; also elsewhere on the board
/Control/5V_ENABLE: U301.28; also elsewhere on the board
/Control/BAT_TEST_ENABLE: U301.15; also elsewhere on the board
/Control/DBG_LED1: D303.2, R301.1, U301.20
/Control/FLASH_POWER_ON_N: Q301.1, R304.2, U301.11
/Control/HK_BAT_V: U301.14; also elsewhere on the board
/Control/LOADCELL_SPI_CS: U301.38; also elsewhere on the board
/Control/QSPI_CSN: R302.2, U301.12, U302.1
/Control/QSPI_IO0: U301.19, U302.5
/Control/QSPI_IO1: U301.18, U302.2
/Control/QSPI_IO2: U301.17, U302.3
/Control/QSPI_IO3: U301.16, U302.7
/Control/QSPI_SCK: U301.13, U302.6
/Control/RFID_CLK: U301.31; also elsewhere on the board
/Control/RFID_DATA: U301.30; also elsewhere on the board
/Control/SPI_CLK: U301.39; also elsewhere on the board
/Control/SPI_MISO: U301.40; also elsewhere on the board
/Control/SPI_MOSI: U301.41; also elsewhere on the board
/Load_Cell/DRDY_N: R303.2; also elsewhere on the board
/Load_Cell/EXC_A_N: U301.46; also elsewhere on the board
/Load_Cell/EXC_A_P: U301.45; also elsewhere on the board
/Load_Cell/EXC_B_N: U301.42; also elsewhere on the board
/Load_Cell/EXC_B_P: U301.43; also elsewhere on the board
/RFID_SLEEP_N: U301.27; also elsewhere on the board
/VAA_LDO_EN: U301.29; also elsewhere on the board
BAT_IN: D301.1, J301.1; also elsewhere on the board
GND: C301.2, C302.2, C303.1, C304.1, C305.2, C306.2, C307.2, C308.2, C310.1, C311.1, C312.1, C313.2, D301.2, D302.3, J301.5, J301.6, P301.3, R306.2, U301.8, U301.23, U301.35, U301.44, U301.47, U301.49, U302.4, U302.9, Y301.2, Y301.4; also elsewhere on the board
NRST: C313.1, P301.1, U301.7
unnamed: C301.1, U301.5, Y301.1
unnamed: C302.1, U301.6, Y301.3
unnamed: C303.2, U301.3, Y302.2
unnamed: C304.2, U301.4, Y302.1
unnamed: C310.2, C311.2, L301.2, U301.9
unnamed: C312.2, JP301.2, R302.1, U302.8
unnamed: D303.1, R306.1
unnamed: JP301.1, Q301.3
unnamed: R303.1, U301.2
RTC_OUT_CALIB: P301.6, R301.2
SWCLK: P301.5, U301.37
SWDIO: P301.4, U301.34
USB_D+: D302.2, J301.3, R305.2, U301.33; also elsewhere on the board
USB_D-: D302.1, J301.2, U301.32; also elsewhere on the board
USER_GPIO: U301.10; also elsewhere on the board

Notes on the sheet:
Debugging interface
1.71 V to 3.6 V 3 to 3.6V if USB used!
BOOT0
2.7 - 3.6V
Flash Memory
The exposed metal pad area on the bottom of the package is floating.
Tag Connect Debugger Pins
USB
these are 5V tolerant pins!
For debugging and development:

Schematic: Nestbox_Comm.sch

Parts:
C401: 10u; C_0805_2012Metric
J401, J402: Conn_01x10_Female; PinSocket_1x10_P2.00mm_Vertical_SMD_Pin1Left; MPN 1-2307813-0
R401, R403: 10k; R_0603_1608Metric
R402, R404, R405: DNP; R_0603_1608Metric
U401: Power Switch 2A, 800us soft start; IC_MIC94085YFT-TR; MPN MIC94082YFT-TR
U402: XBEE; MPN SuperBx

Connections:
/Communication/RF_CTS: J402.2, U402.12; also elsewhere on the board
/Communication/RF_ENABLE: R403.2, R404.1, U401.4; also elsewhere on the board
/Communication/RF_RTS: J402.6, U402.16; also elsewhere on the board
/Communication/RF_RX: J401.3, U402.3; also elsewhere on the board
/Communication/RF_TX: J401.2, U402.2; also elsewhere on the board
/Communication/SUPER_B_EN: J401.5, R401.2, R404.2, U402.5
/Communication/SUPER_B_IO0: J401.7, U402.7
/Communication/dtr: J401.9, R402.2, U402.9
GND: C401.2, J401.10, R402.1, R403.1, U401.2, U402.10; also elsewhere on the board
VCOM: C401.1, J401.1, R401.1, R405.2, U401.1, U402.1

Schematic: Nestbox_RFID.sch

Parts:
C501, C503: 10u; C_0805_2012Metric
C502, C504, C507, C508: 100n; C_0603_1608Metric
C505, C506: 10n; C_0603_1608Metric
CRES501: 0R; C_0603_1608Metric
CRES502, CRES503: 1n5 450V C0G; C_0805_2012Metric; MPN CGA4F4C0G2W152J085AE
Cdiv501: 10p 500V; C_0805_2012Metric; MPN C0805C100JDGACTU
Cdiv502: 1n; C_0603_1608Metric
J501: Conn_RFID_UFL_ALT; U.FL_Hirose_U.FL-R-SMT-1_Vertical; MPN U.FL-R-SMT(10)
J502: Conn_RFID_SMA; SMA_Molex_EdgeMount; MPN 0732512120
Q501: NMOS 30V 4A; SOT-23; MPN SI2316DS-T1-E3
R501, R502, R507, R508: 0R; R_0603_1608Metric
R503, R505, R506, R509: DNP; R_0603_1608Metric
R504: 82k; R_0603_1608Metric
U501: EM4095; SOIC-16_3.9x9.9mm_P1.27mm; MPN EM4095

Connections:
+5V: C501.1, C502.1, C503.2, C504.2, R504.2, U501.4, U501.7; also elsewhere on the board
/Control/RFID_CLK: R506.2, R507.1; also elsewhere on the board
/Control/RFID_DATA: R508.2, R509.1; also elsewhere on the board
/RFID/ant1: J501.1, J502.1, R501.1
/RFID/ant2: CRES501.2, Cdiv501.2, J501.2, J502.2
/RFID/demod_out: R507.2, U501.13
/RFID/rdyclk: R508.1, U501.2
/RFID/shd: Q501.3 (D), R503.1, R504.1, R505.1, U501.14
/RFID_SLEEP_N: Q501.1 (G), R503.2; also elsewhere on the board
GND: C501.2, C502.2, C503.1, C504.1, C505.1, C506.1, C507.1, Cdiv502.1, Q501.2 (S), R502.1, R505.2, R506.1, R509.2, U501.1, U501.5; also elsewhere on the board
unnamed: C505.2, U501.16
unnamed: C506.2, U501.15
unnamed: C507.2, U501.11
unnamed: C508.1, U501.9
unnamed: C508.2, U501.10
unnamed: CRES501.1, CRES502.2
unnamed: CRES502.1, CRES503.2
unnamed: CRES503.1, U501.6
unnamed: Cdiv501.1, Cdiv502.2, U501.8
unnamed: R501.2, U501.3
unnamed: R502.2, U501.12

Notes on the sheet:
USE 5V TOLERANT PINS!

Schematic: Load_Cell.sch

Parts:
C601, C603, C604: 100n 1% DNP; C_0603_1608Metric
C602: 1u DNP; C_0603_1608Metric
C605, C607: 100n DNP; C_0603_1608Metric
C606, C609: 100n; C_0603_1608Metric
C608: 1u; C_0603_1608Metric
C610: 10u; C_0805_2012Metric
C611: 10n; C_0603_1608Metric
J601: LOAD_CELL_CONN_01X04; MB08MBSAFF04RA; MPN M8S-04PMMR-SF8001
J602: LOAD_CELL_CONN_01X04; Molex_PicoBlade_53398-0471_1x04-1MP_P1.25mm_Vertical; MPN 53398-0471
Q601, Q603: DMG2301L-7; SOT-23; MPN DMG2301L-7
Q602, Q604: NMOS 30V 4A; SOT-23; MPN SI2316DS-T1-E3
R601, R602, R603, R604: 82k; R_0603_1608Metric
R605, R606, R607, R608, R609, R610, R611, R612, R618: 0R; R_0603_1608Metric
R613, R614: DNP; R_0603_1608Metric
R615, R616, R617: 47R; R_0603_1608Metric
U601: ADS1220; TSSOP-16_4.4x5mm_P0.65mm; MPN ADS1220IPW
U602: SIT1602BI 4.096 MHz; Oscillator_SMD_EuroQuartz_XO32-4Pin_3.2x2.5mm; MPN SIT1602BI-21-XXE-4.096000

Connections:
/ADC_CLK_EN: R613.1, U602.1; also elsewhere on the board
/Control/LOADCELL_SPI_CS: U601.2 (~CS); also elsewhere on the board
/Control/SPI_CLK: R615.1; also elsewhere on the board
/Control/SPI_MISO: R617.1; also elsewhere on the board
/Control/SPI_MOSI: R616.1; also elsewhere on the board
/Load_Cell/ADC_CLK: R614.1, R618.2, U601.3 (CLK)
/Load_Cell/AIN1: C604.2, R608.1, U601.10 (AIN1)
/Load_Cell/AIN2: C604.1, R607.1, U601.7 (AIN2)
/Load_Cell/DRDY_N: U601.14 (~DRDY); also elsewhere on the board
/Load_Cell/EXC_A: C601.1, C602.1, J601.1, J602.1, R605.1, R609.2
/Load_Cell/EXC_A_N: Q602.1, R602.2; also elsewhere on the board
/Load_Cell/EXC_A_P: Q601.1, R601.1; also elsewhere on the board
/Load_Cell/EXC_B: C602.2, C603.1, J601.3, J602.3, R606.1, R610.2
/Load_Cell/EXC_B_N: Q604.1, R604.2; also elsewhere on the board
/Load_Cell/EXC_B_P: Q603.1, R603.1; also elsewhere on the board
/Load_Cell/green: J601.2, J602.2, R607.2
/Load_Cell/white: J601.4, J602.4, R608.2
GND: C601.2, C603.2, C606.2, C608.2, C609.1, C610.1, C611.1, J601.SH, Q602.2, Q604.2, R602.1, R604.1, R614.2, U601.4 (DGND), U601.5 (AVSS), U602.2; also elsewhere on the board
unnamed: C605.1, R609.1, R612.2, U601.11 (AIN0/REFP1)
unnamed: C605.2, R610.1, R611.2, U601.6 (AIN3/REFN1)
unnamed: C607.1, R611.1, U601.9 (REFP0)
unnamed: C607.2, R612.1, U601.8 (REFN0)
unnamed: Q601.3, Q602.3, R605.2
unnamed: Q603.3, Q604.3, R606.2
unnamed: R615.2, U601.1 (SCLK)
unnamed: R616.2, U601.16 (DIN)
unnamed: R617.2, U601.15 (DOUT/~DRDY)
unnamed: R618.1, U602.3
VAA: C610.2, C611.2, Q601.2, Q603.2, R601.2, R603.2, U601.12 (AVDD); also elsewhere on the board

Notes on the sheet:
cut-off frequency not too low to allow 1 kHz PWM sampling
X2YTM capacitors were used for the RC low-pass filters. A single X2YTM capacitor can replace multiple capacitors required for common-mode and differential filtering. In addition to saving board space, these capacitors have low equivalent series inductance (ESL) and excellent common-mode capacitor m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
!! high RC resistors result in high input offset from differential bias currents !!
Typically common-mode filters become mismatched because of high capacitor tolerances. Higher common-mode signal frequencies are then filtered differently and result in a differential signal seen by the ADC inputs. This effect can also be reduced by ensuring that the differential filter has a lower 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
using a first-order RC filter with a cutoff frequency set at the output data rate or 10x higher is generally a good start —> ca 20 - 200 Hz when in exact mode
performance "seems" better with 0R resistor here!
Connector Numbering is according to Finecables cable assembly A2330-CP-T0005
red green black white
Connector Numbering Not confirmed.

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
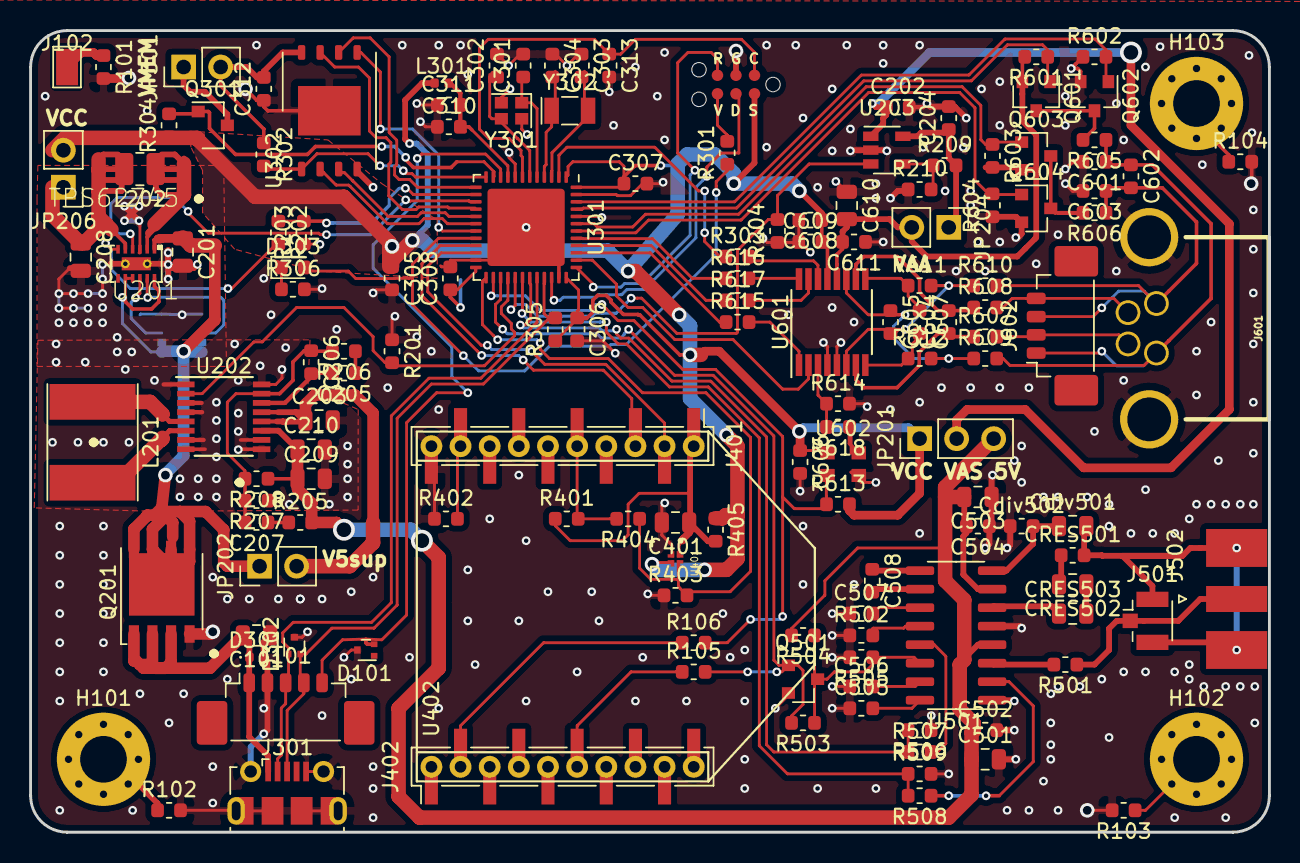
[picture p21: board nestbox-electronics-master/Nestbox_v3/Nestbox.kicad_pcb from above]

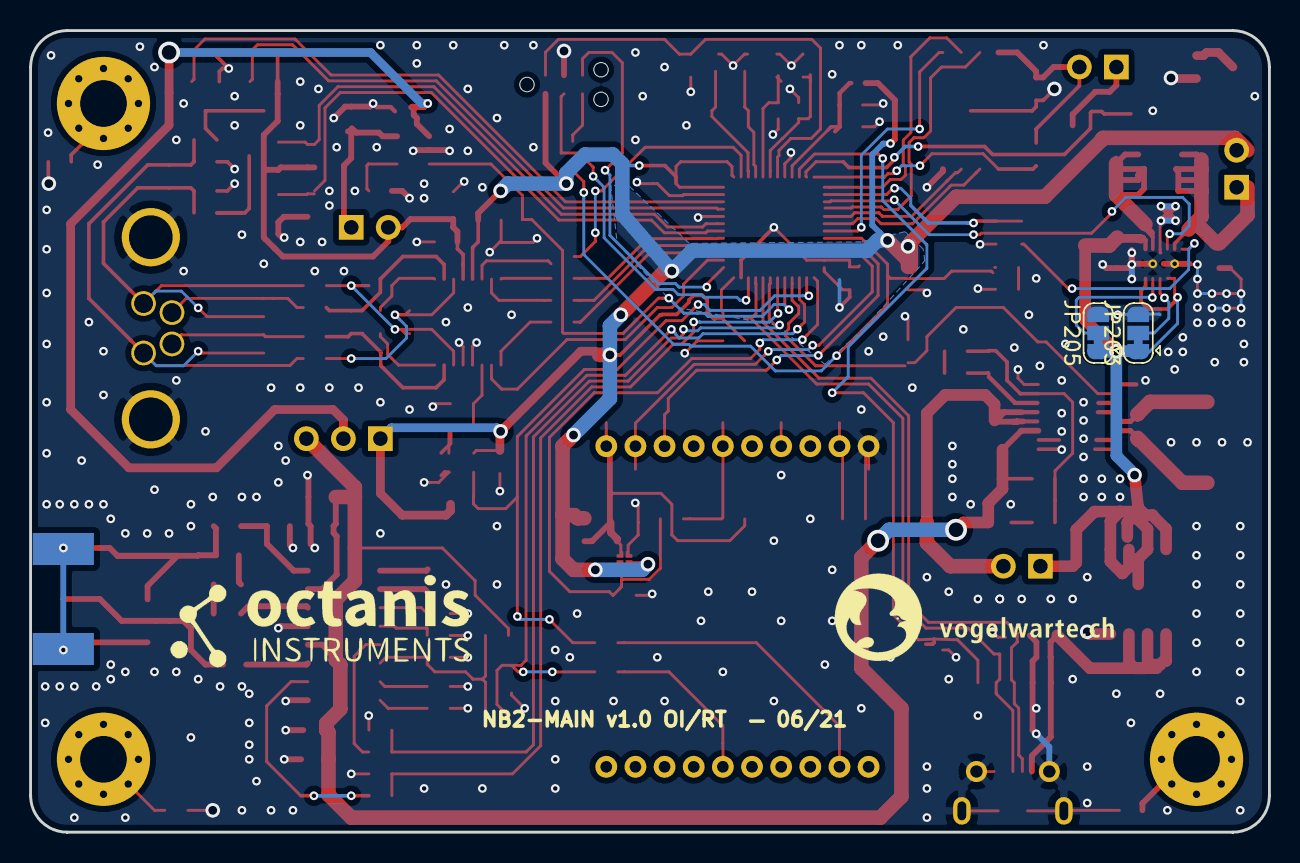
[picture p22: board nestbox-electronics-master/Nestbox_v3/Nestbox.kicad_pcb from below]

Board: 2 copper layers, 85.0 x 55.0 mm, 150 parts (4 on the bottom side), 108 nets.

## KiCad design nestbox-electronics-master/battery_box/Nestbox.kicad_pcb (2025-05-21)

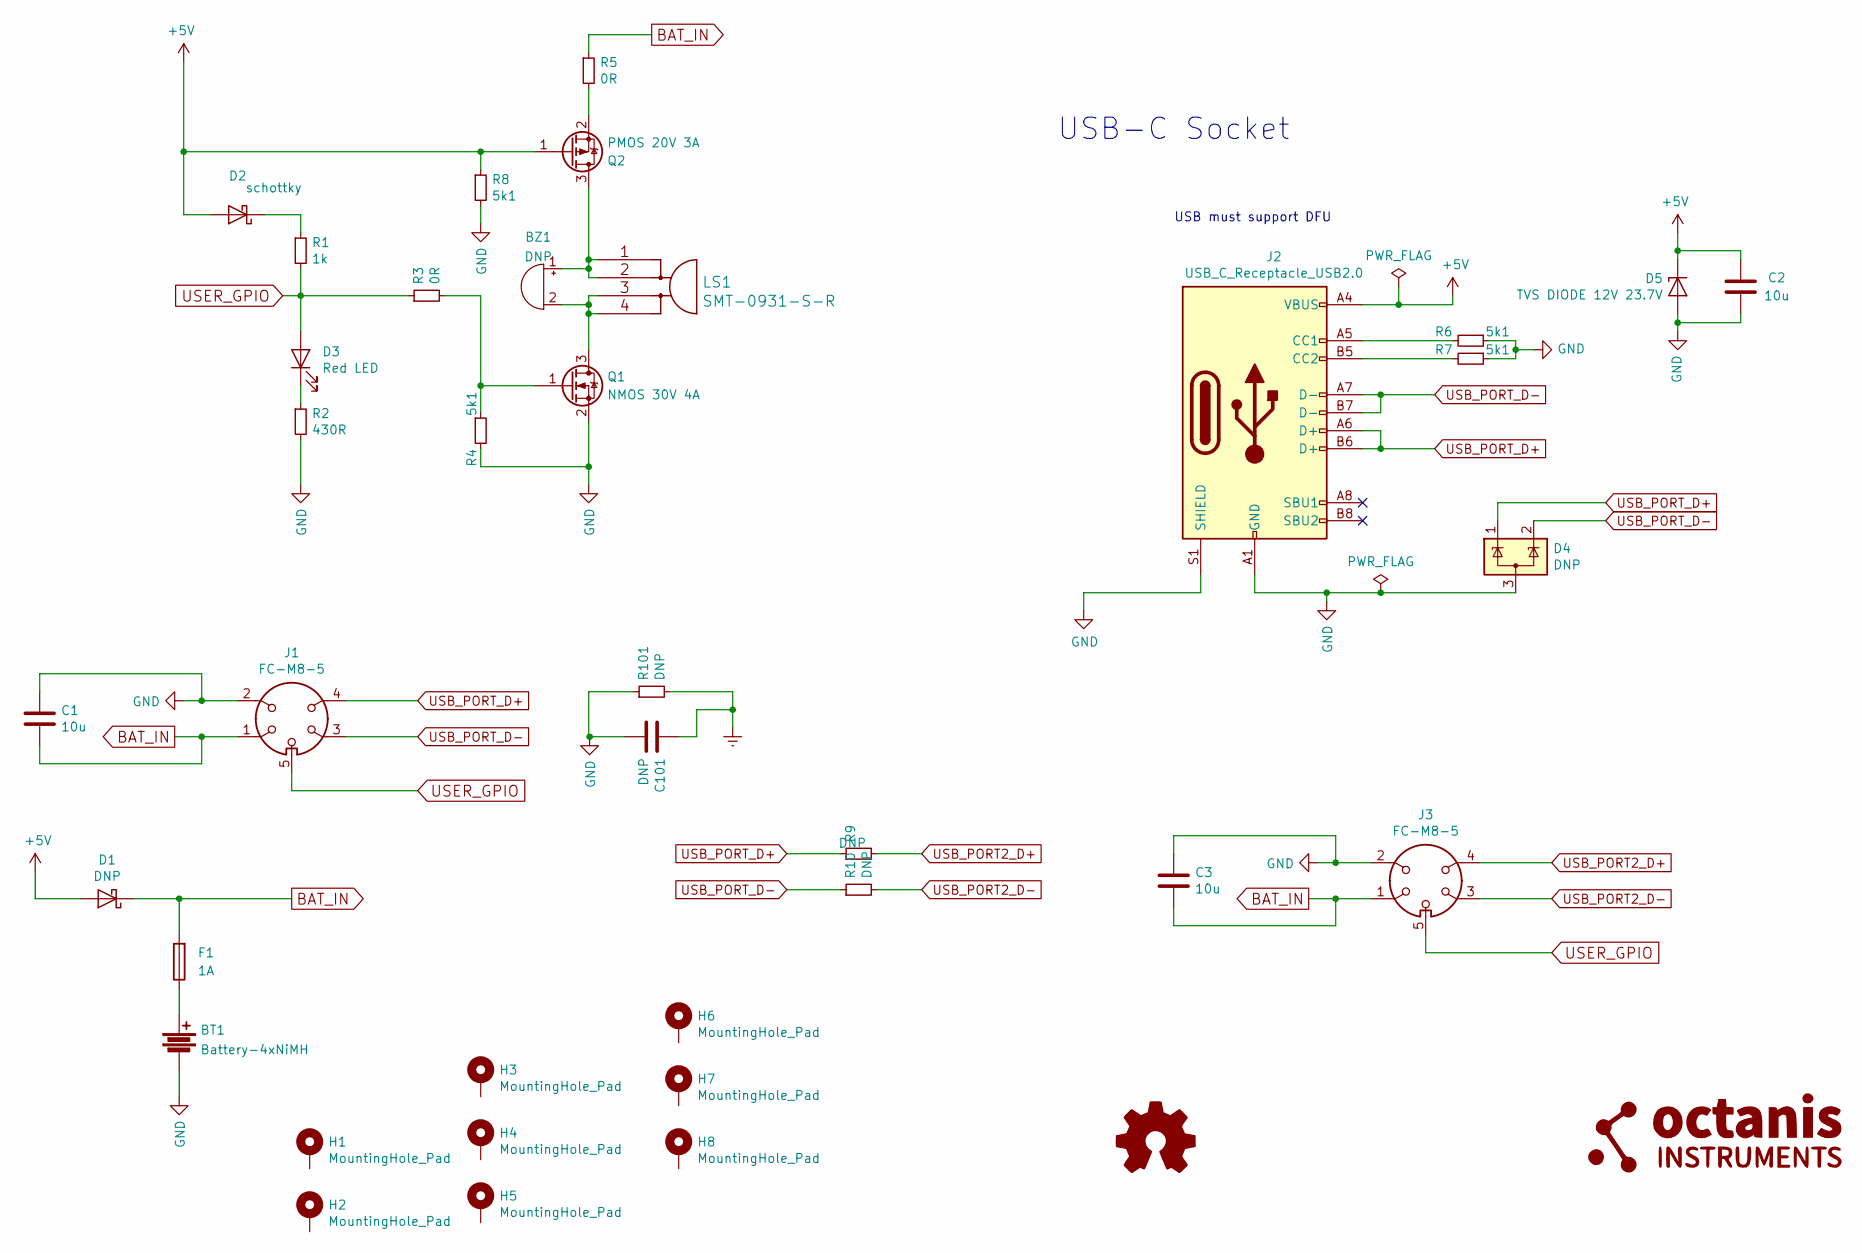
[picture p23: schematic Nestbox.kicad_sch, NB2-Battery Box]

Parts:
BT1: Battery-4xNiMH; TerminalBlock_Dinkle_DT-55-B01X-02_P10.00mm
BZ1: DNP; Buzzer_CUI_CPT-9019S-SMT; MPN SMT-0827-SW-5V-R
C1, C2, C3: 10u; C_0805_2012Metric
C101: DNP; C_0805_2012Metric
D1: DNP; D_SOD-323; MPN B0520WS-7-F
D2: schottky; D_SOD-323; MPN B0520WS-7-F
D3: Red LED; LED_D5.0mm; MPN WP934EW/ID
D4: DNP; SOT-723; MPN SZESD7205DT5G
D5: TVS DIODE 12V 23.7V; D_SOD-523; MPN UCLAMP1201H.TCT
F1: 1A; 0154001.DR; MPN 0154001.DR
G1: LOGO; oi_logo_small
H1, H3, H5, H7: MountingHole_Pad; MountingHole_4.5mm
H2, H4, H6, H8: MountingHole_Pad; MountingHole_3.5mm
J1, J3: FC-M8-5; M8-5pin_2.9mm_hole; MPN2 1424240
J2: USB_C_Receptacle_USB2.0; USB_C_Receptacle_HRO_TYPE-C-31-M-12; MPN USB4105-GF-A
LOGO1: Logo_Open_Hardware_Small; VogelwarteLogo3
LS1: SMT-0931-S-R; MPN SMT-0931-S-R
Q1: NMOS 30V 4A; SOT-23; MPN PMV45EN2R
Q2: PMOS 20V 3A; SOT-23; MPN DMP2160U-7
R1: 1k; R_0603_1608Metric
R2: 430R; R_0603_1608Metric
R3, R5: 0R; R_0603_1608Metric
R4, R6, R7, R8: 5k1; R_0603_1608Metric
R9, R10, R101: DNP; R_0603_1608Metric

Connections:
+5V: C2.1, D1.2 (A), D2.2 (A), D5.1 (K), J2.A4 (VBUS), J2.A9 (VBUS), J2.B4 (VBUS), J2.B9 (VBUS), Q2.1 (G), R8.1
BAT_IN: C1.2, C3.2, D1.1 (K), F1.2, J1.1, J3.1, R5.1
Earth: C101.1, R101.2
GND: BT1.2, C1.1, C2.2, C3.1, C101.2, D4.3 (A), D5.2 (A), J1.2, J2.A1 (GND), J2.A12 (GND), J2.B1 (GND), J2.B12 (GND), J2.S1 (SHIELD), J3.2, Q1.2 (S), R2.2, R4.2, R6.1, R7.1, R8.2, R101.1
unnamed: BT1.1, F1.1
unnamed: BZ1.1 (-), LS1.1, LS1.2, Q2.3 (D)
unnamed: BZ1.2 (+), LS1.3, LS1.4, Q1.3 (D)
unnamed: D2.1 (K), R1.1
unnamed: D3.1 (K), R2.1
unnamed: J2.A5 (CC1), R6.2
unnamed: J2.B5 (CC2), R7.2
unnamed: Q1.1 (G), R3.2, R4.1
unnamed: Q2.2 (S), R5.2
USB_PORT2_D+: J3.4, R9.2
USB_PORT2_D-: J3.3, R10.2
USB_PORT_D+: D4.1 (K), J1.4, J2.A6 (D+), J2.B6 (D+), R9.1
USB_PORT_D-: D4.2 (K), J1.3, J2.A7 (D-), J2.B7 (D-), R10.1
USER_GPIO: D3.2 (A), J1.5, J3.5, R1.2, R3.1

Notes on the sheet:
USB-C Socket
USB must support DFU

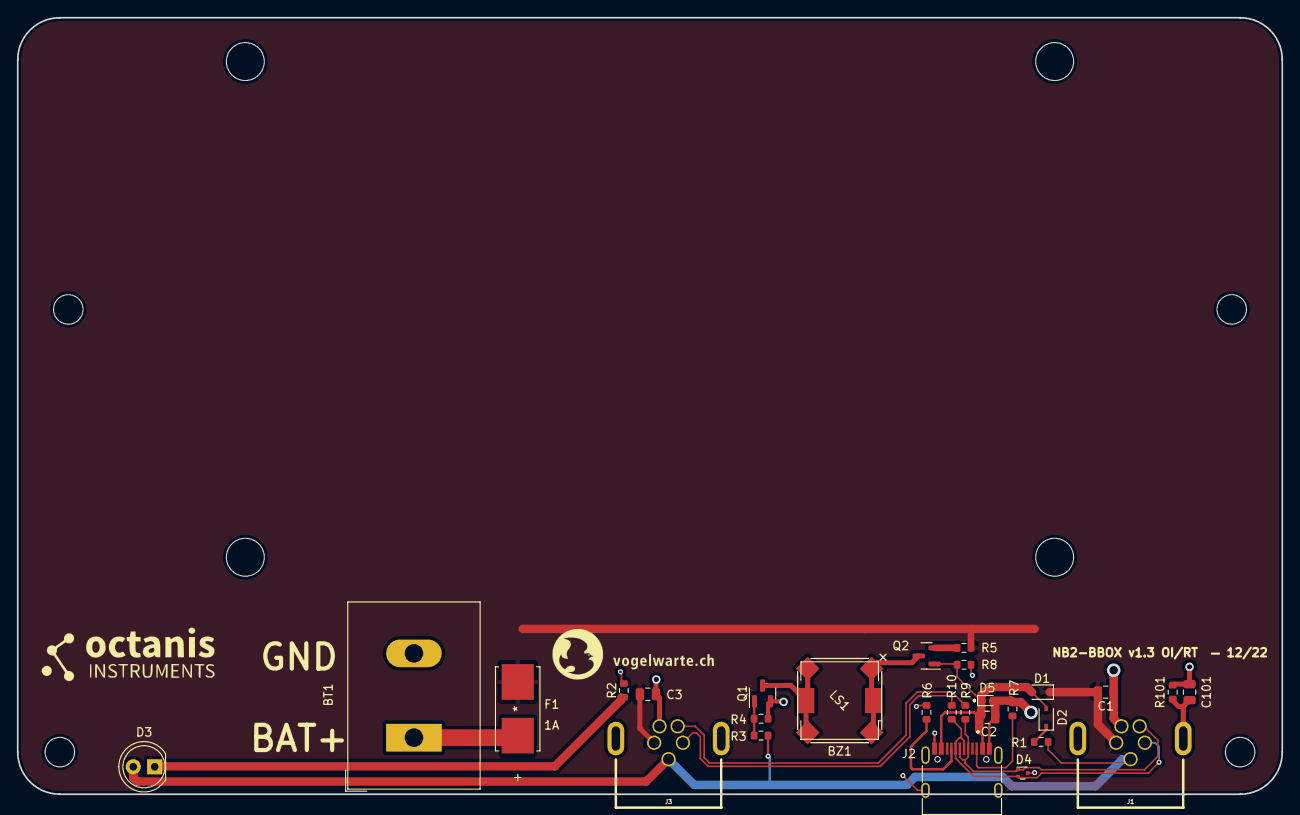
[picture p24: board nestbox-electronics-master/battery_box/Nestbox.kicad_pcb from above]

Board: 2 copper layers, 150.0 x 92.1 mm, 39 parts (0 on the bottom side), 18 nets.

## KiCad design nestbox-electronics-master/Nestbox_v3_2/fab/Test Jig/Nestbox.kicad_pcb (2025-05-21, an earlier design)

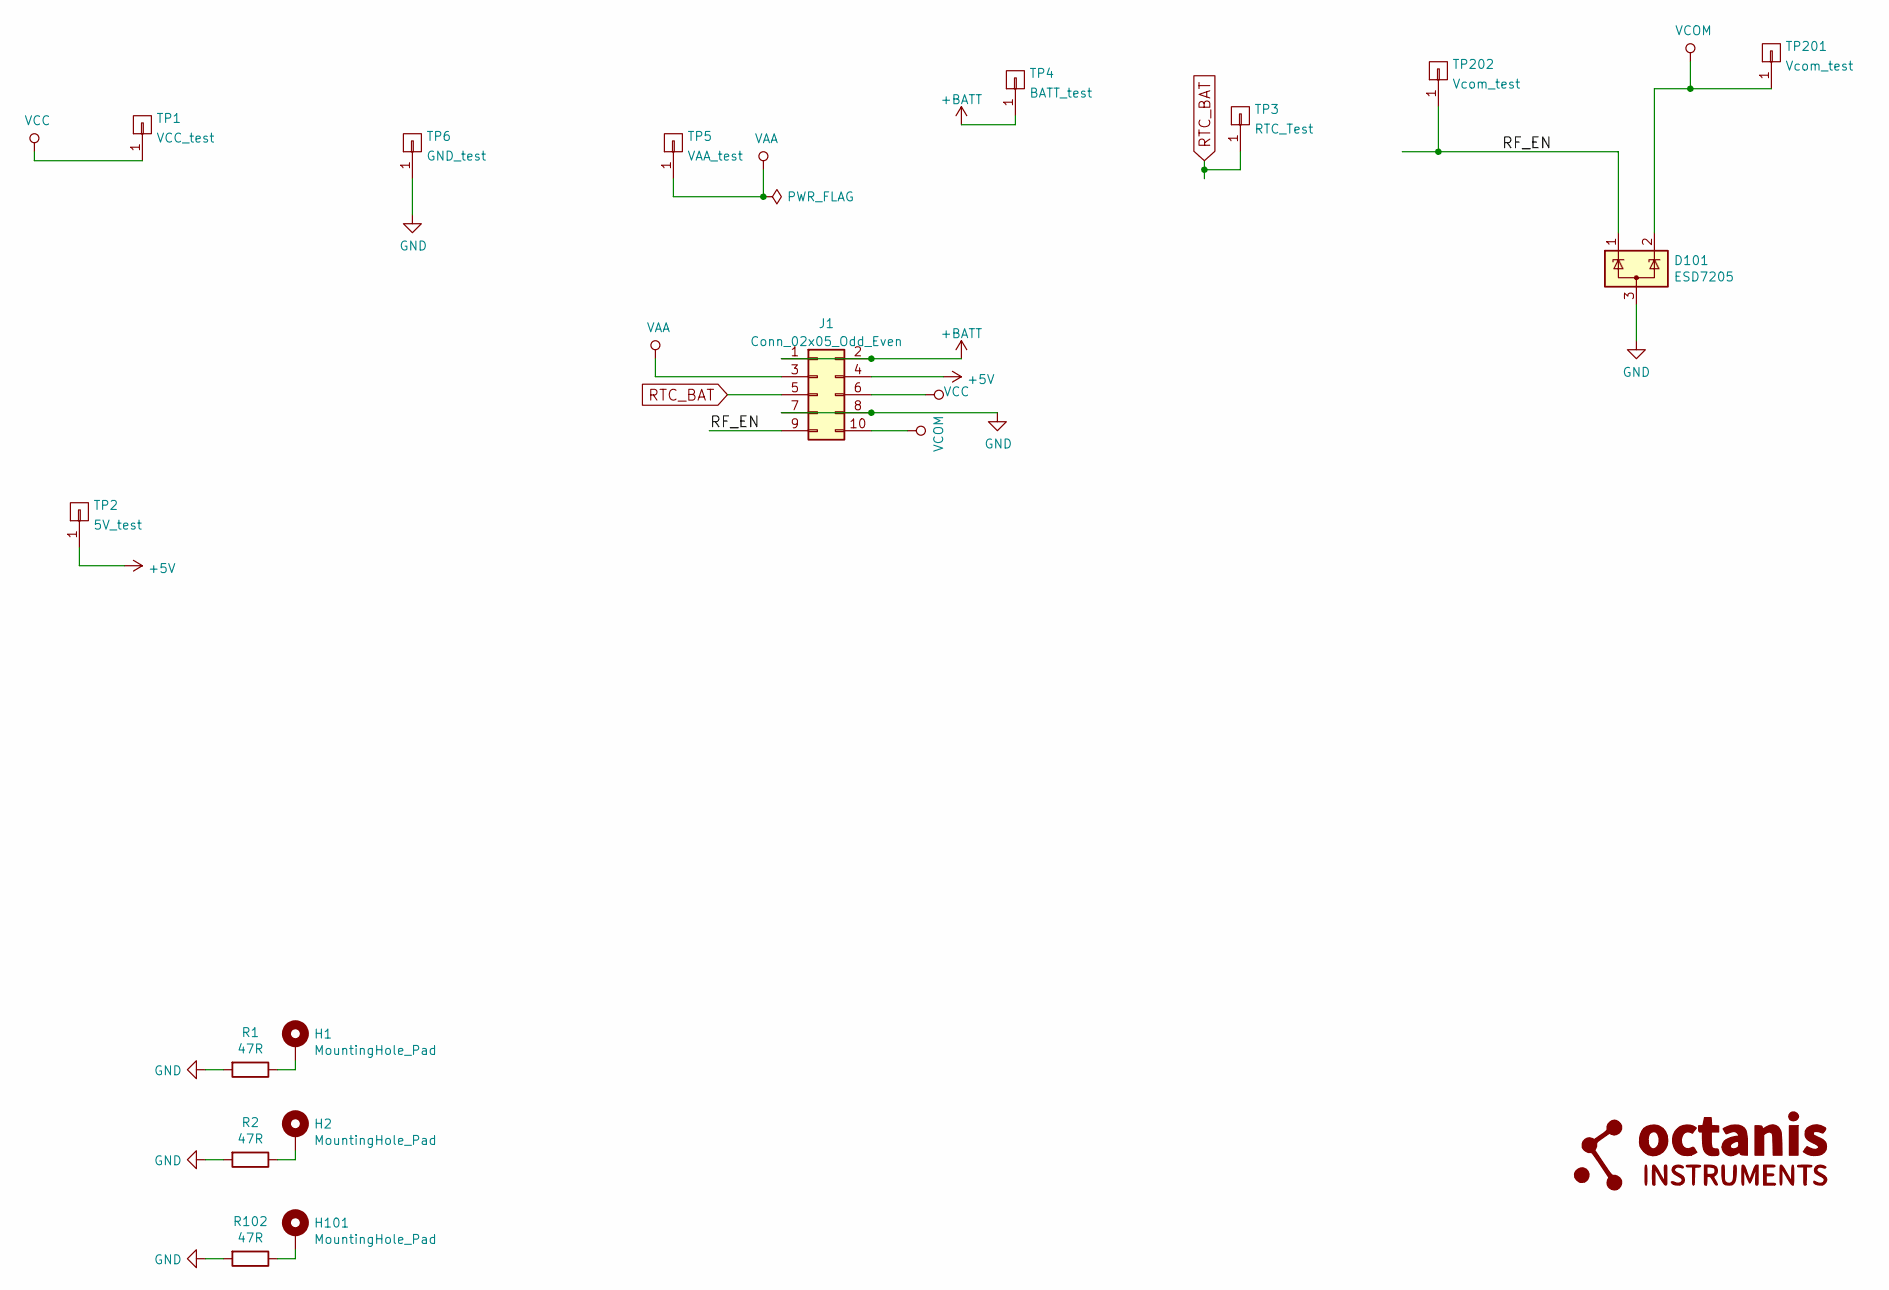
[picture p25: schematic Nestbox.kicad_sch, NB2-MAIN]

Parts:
D101: ESD7205; SOT-723; MPN SZESD7205DT5G
G101: LOGO; oi_logo_small
H1, H2, H101: MountingHole_Pad; MountingHole_2.5mm_Pad
J1: Conn_02x05_Odd_Even; IDC-Header_2x05_P2.54mm_Horizontal
R1, R2, R102: 47R; R_0603_1608Metric
TP1: VCC_test; Pin_D0.7mm_L6.5mm_W1.8mm_FlatFork
TP2: 5V_test; Pin_D0.7mm_L6.5mm_W1.8mm_FlatFork
TP3: RTC_Test; Pin_D0.7mm_L6.5mm_W1.8mm_FlatFork
TP4: BATT_test; Pin_D0.7mm_L6.5mm_W1.8mm_FlatFork
TP5: VAA_test; Pin_D0.7mm_L6.5mm_W1.8mm_FlatFork
TP6: GND_test; Pin_D0.7mm_L6.5mm_W1.8mm_FlatFork
TP201, TP202: Vcom_test; Pin_D0.7mm_L6.5mm_W1.8mm_FlatFork

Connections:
+5V: J1.4, TP2.1
+BATT: J1.1, J1.2, TP4.1
/RF_EN: D101.1 (K), J1.9, TP202.1
GND: D101.3 (A), J1.7, J1.8, R1.2, R2.2, R102.2, TP6.1
unnamed: H1.1, R1.1
unnamed: H2.1, R2.1
unnamed: H101.1, R102.1
RTC_BAT: J1.5, TP3.1
VAA: J1.3, TP5.1
VCC: J1.6, TP1.1
VCOM: D101.2 (K), J1.10, TP201.1

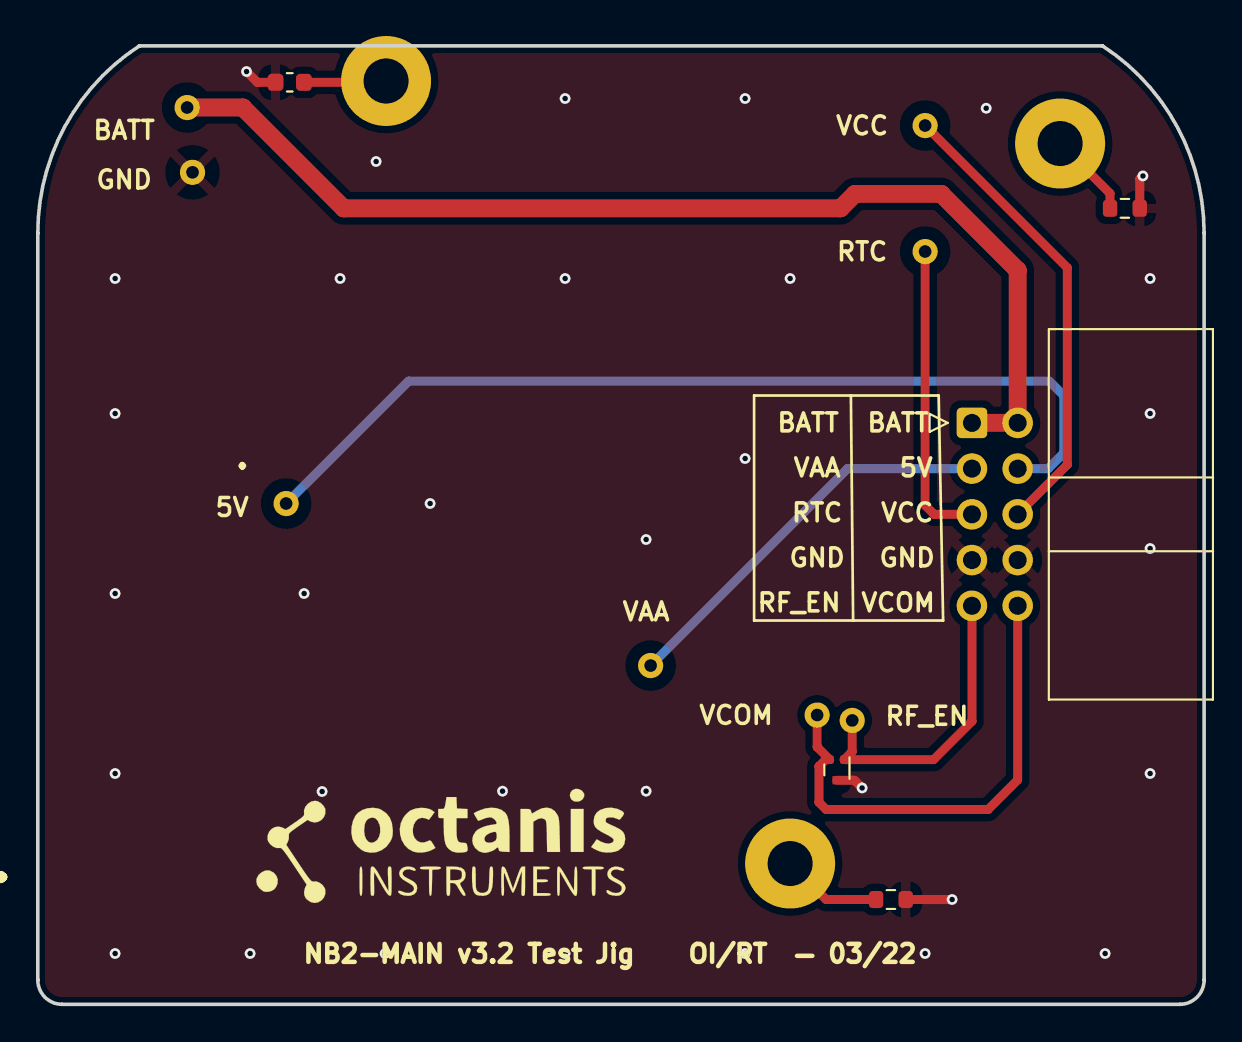
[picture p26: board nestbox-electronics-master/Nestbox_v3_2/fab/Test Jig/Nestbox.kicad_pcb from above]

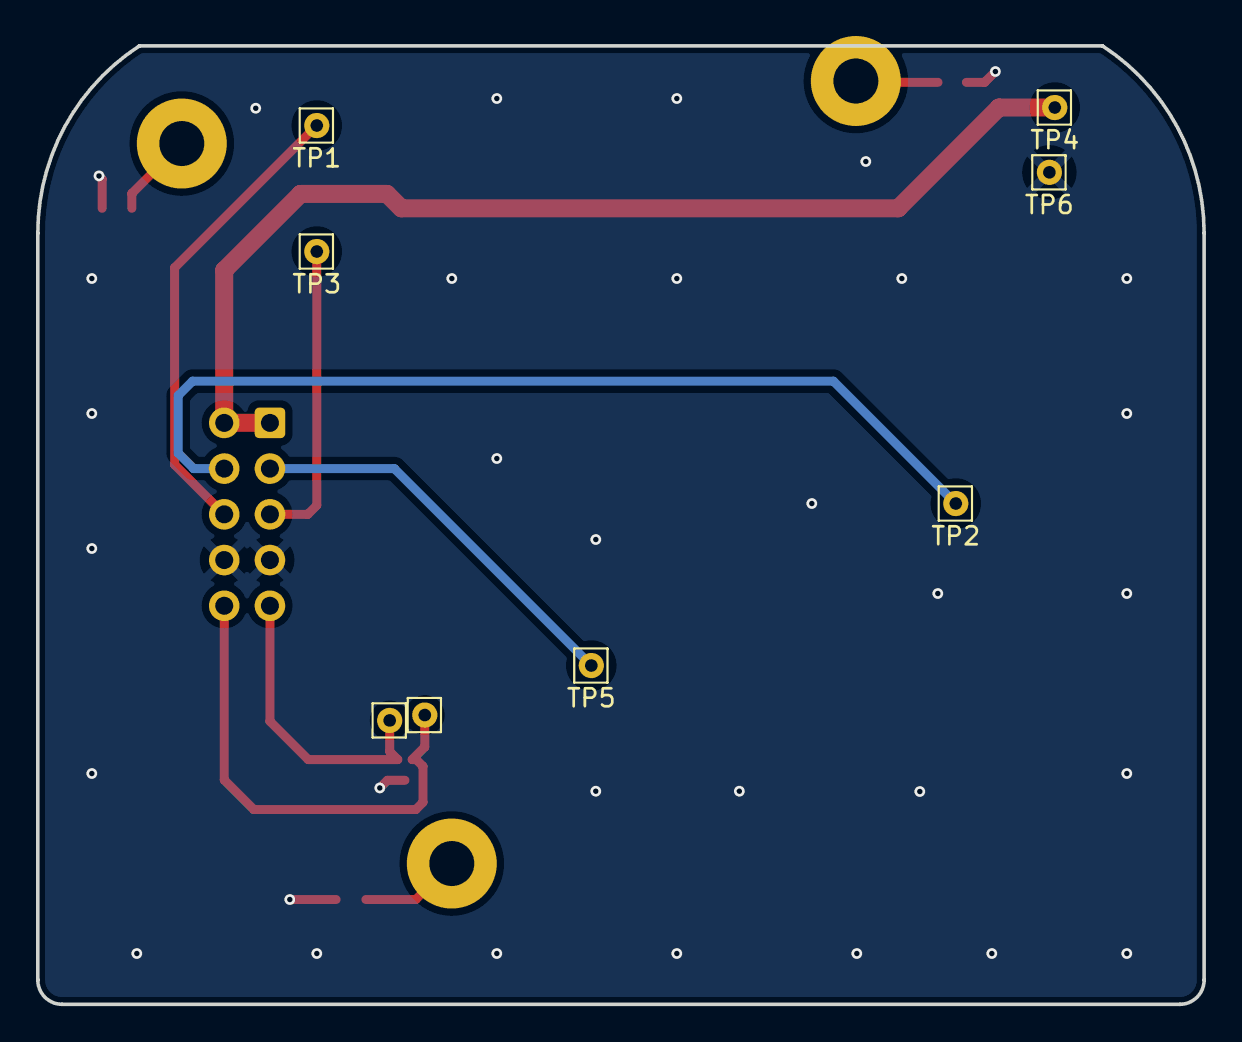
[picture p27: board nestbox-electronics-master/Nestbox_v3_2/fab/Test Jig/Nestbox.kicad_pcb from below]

Board: 2 copper layers, 64.8 x 53.2 mm, 17 parts (8 on the bottom side), 11 nets.

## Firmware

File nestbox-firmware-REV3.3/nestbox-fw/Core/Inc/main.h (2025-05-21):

/* USER CODE BEGIN Header */
/**
  ******************************************************************************
  * @file           : main.h
  * @brief          : Header for main.c file.
  *                   This file contains the common defines of the application.
  ******************************************************************************
  * @attention
  *
  * <h2><center>&copy; Copyright (c) 2021 STMicroelectronics.
  * All rights reserved.</center></h2>
  *
  * This software component is licensed by ST under Ultimate Liberty license
  * SLA0044, the "License"; You may not use this file except in compliance with
  * the License. You may obtain a copy of the License at:
  *                             www.st.com/SLA0044
  *
  ******************************************************************************
  */
/* USER CODE END Header */

/* Define to prevent recursive inclusion -------------------------------------*/
#ifndef __MAIN_H
#define __MAIN_H

#ifdef __cplusplus
extern "C" {
#endif

/* Includes ------------------------------------------------------------------*/
#include "stm32l4xx_hal.h"

/* Private includes ----------------------------------------------------------*/
/* USER CODE BEGIN Includes */
#define NAND_FLASH_USE_LEGACY_FTL	// allows to use FTL with continuous logs written to flash, instead of accessing specific sectors.

/* USER CODE END Includes */

/* Exported types ------------------------------------------------------------*/
/* USER CODE BEGIN ET */

/* USER CODE END ET */

/* Exported constants --------------------------------------------------------*/
/* USER CODE BEGIN EC */
#define DEBUG_LED_OFF	0
#define DEBUG_LED_ON	0 // TODO-PROD: keep LED off in production code.
/* USER CODE END EC */

/* Exported macro ------------------------------------------------------------*/
/* USER CODE BEGIN EM */
#define PWR_LOAD_CELL_LDO_EN_GPIO_Port 	PWR_GPIO_A
#define PWR_BAT_TEST_EN_GPIO_Port 		PWR_GPIO_A
#warning "These constants are not updated. Check with port names below"
/* USER CODE END EM */

/* Exported functions prototypes ---------------------------------------------*/
void Error_Handler(void);

/* USER CODE BEGIN EFP */
void system_restore_clock();
/* USER CODE END EFP */

/* Private defines -----------------------------------------------------------*/
#define LOADCELL_DRDY_N_Pin GPIO_PIN_13
#define LOADCELL_DRDY_N_GPIO_Port GPIOC
#define LOADCELL_DRDY_N_EXTI_IRQn EXTI15_10_IRQn
#define USER_GPIO_Pin GPIO_PIN_0
#define USER_GPIO_GPIO_Port GPIOA
#define USER_GPIO_EXTI_IRQn EXTI0_IRQn
#define FLASH_POWER_ON_N_Pin GPIO_PIN_1
#define FLASH_POWER_ON_N_GPIO_Port GPIOA
#define VBAT_ADC9_Pin GPIO_PIN_4
#define VBAT_ADC9_GPIO_Port GPIOA
#define BAT_TEST_EN_Pin GPIO_PIN_5
#define BAT_TEST_EN_GPIO_Port GPIOA
#define DEBUG_LED_RTC_CALIB_Pin GPIO_PIN_2
#define DEBUG_LED_RTC_CALIB_GPIO_Port GPIOB
#define WIFI_EN_Pin GPIO_PIN_12
#define WIFI_EN_GPIO_Port GPIOB
#define ADC_CLK_EN_Pin GPIO_PIN_13
#define ADC_CLK_EN_GPIO_Port GPIOB
#define RFID_SHDN_Pin GPIO_PIN_14
#define RFID_SHDN_GPIO_Port GPIOB
#define RFID_SUPPLY_EN_Pin GPIO_PIN_15
#define RFID_SUPPLY_EN_GPIO_Port GPIOB
#define LOAD_CELL_LDO_EN_Pin GPIO_PIN_8
#define LOAD_CELL_LDO_EN_GPIO_Port GPIOA
#define LOADCELL_CS_N_Pin GPIO_PIN_15
#define LOADCELL_CS_N_GPIO_Port GPIOA
#define EXC_B_N_Pin GPIO_PIN_6
#define EXC_B_N_GPIO_Port GPIOB
#define EXC_B_P_Pin GPIO_PIN_7
#define EXC_B_P_GPIO_Port GPIOB
#define EXC_A_P_Pin GPIO_PIN_8
#define EXC_A_P_GPIO_Port GPIOB
#define EXC_A_N_Pin GPIO_PIN_9
#define EXC_A_N_GPIO_Port GPIOB
/* USER CODE BEGIN Private defines */

/* USER CODE END Private defines */

#ifdef __cplusplus
}
#endif

#endif /* __MAIN_H */

/************************ (C) COPYRIGHT STMicroelectronics *****END OF FILE****/

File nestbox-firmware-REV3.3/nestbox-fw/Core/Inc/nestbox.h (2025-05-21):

/*
 * nestbox.h
 *
 *  Created on: 15 Sep 2021
 *      Author: raffael
 */

#ifndef INC_NESTBOX_H_
#define INC_NESTBOX_H_

#include "oi_gitcommit.h"

/******************** Main configurations: **************************/
//#define DEBUG_WITHOUT_COMM_MODULE
//#define NB_CONSTANT_CALIBRATION_MODE
#define USE_LOW_POWER_MODE
#define NB_DAYTIME_POWER_OFF 	//comment if system shall be on 24/24h
//#define NB2_EMC_TEST_MODE		// uncomment for emission testing
/********************************************************************/

// Version info
#define NB_HW_VERSION					0x33
#define NB_FW_VERSION					OI_GIT_HEAD

// Load cell defaults:
#define NB_DETECTION_THRESHOLD			50		// grams
#define NB_OVERLOAD_THRESHOLD			2000	// grams
#define NB_MAX_STDEV_FOR_VALID_SAMPLE	5	// grams
#define NB_MAX_DIFF_FOR_VALID_SAMPLE	5	// maximum grams of difference between two samples to be considered valid.

#define NB_OFFSET_SIGNIFICANT_CHANGE	2	// grams

#define NB_LOAD_CELL_DEFAULT_SLOPE		500	// ADC counts per gram
#define NB_LOAD_CELL_DEFAULT_INTERCEPT	0	// ADC counts

// Calibration defaults:
#define NB_N_CALIBRATION_WEIGHTS			4
#define NB_CAL_W0							100.0
#define NB_CAL_W1							200.0
#define NB_CAL_W2							500.0
#define NB_CAL_W3							1000.0
#define NB_CALIBRATION_WEIGHTS_TOL			0.25 	// fraction; load cell has a sensitivity tolerance of 10%; then temperature effects need to be taken into account as well.

#define NB_DEFAULT_CALIBRATION_WEIGHTS 		{NB_CAL_W0,NB_CAL_W1,NB_CAL_W2,NB_CAL_W3} // in grams, floating point
#define NB_CALIBRATION_WEIGHTS_TOLERANCES	{NB_CAL_W0 * NB_CALIBRATION_WEIGHTS_TOL, NB_CAL_W1 * NB_CALIBRATION_WEIGHTS_TOL, \
											NB_CAL_W2 * NB_CALIBRATION_WEIGHTS_TOL, NB_CAL_W3 * NB_CALIBRATION_WEIGHTS_TOL} // in grams, floating point


#define NB_N_MINIMUM_CALIBRATION_WEIGHTS	3	// minimum number of weights to be used for calibration
#define NB_LINREG_MIN_R2					0.999f


// Power Management:
#define VBAT_FULL_MV		5400 // value used to calculate battery percentage (empirical from field study)
#define VBAT_EMPTY_MV		4500 // value used to calculate battery percentage (empirical from field study)
#define VBAT_SHUTDOWN_MV	4500 // system sends a last comm message before going to deep sleep
#define VBAT_STARTUP_MIN_MV	4600 // system will not boot from POR if battery voltage is below this value.

#define VBAT_SHUTDOWN_THRESHOLD_COUNTER		6


// Daytime power-off management:
#define NB_DAYTIME_POWER_OFF_HOUR_UTC	8	// system will switch off at 8am UTC (9am CET, 10am CEST)
#define NB_DAYTIME_POWER_ON_HOUR_UTC	16	// system will switch on at 4pm UTC (5pm CET, 6pm CEST)


// Timeout values in number of retries
#define NB_RFID_RETRY_TIMEOUT				10
#define NB_OFFSET_UNSTABLE_RETRY_TIMEOUT	10
#define NB_GET_TIME_RETRY_TIMEOUT			3

// Time values in milliseconds
#define RFID_READER_ON_TIME_MS		500
// Time values in seconds:
#define NB_RFID_RETRY_PERIOD		3
#define NB_EVENT_MAX_DURATION		240
// intervals in seconds:
#define NB_LOAD_CELL_POLLING_PERIOD	1
#define	NB_OFFSET_MEAS_PERIOD		180
#define NB_OFFSET_MAX_TX_PERIOD		7200//14400	// transmit offset at least every 4 hours
#define NB_OFFSET_MIN_TX_PERIOD		3600	// transmit offset at most every 1 hour

#define	NB_STATUS_MEAS_PERIOD		180
#define	NB_STATUS_TX_PERIOD			28800	// transmit status every 8 hours
#define NB_GET_TIME_RETRY_PERIOD	1800	// if base station did not reply, retry fetching the time.
#define NB_AUTO_END_CALIB_STATE		3600	// after 1 hour, the system automatically exits calibration mode

#define NB_EVENT_N_SAMPLES			19	// preferably an uneven number (for median calculation)
#define NB_OFFSET_N_SAMPLES			11	// must be smaller than NB_EVENT_N_SAMPLES!
											// + preferably an uneven number (for median calculation)
#if(NB_OFFSET_N_SAMPLES > NB_EVENT_N_SAMPLES)
#error("NB_EVENT_N_SAMPLES must be larger than or equal NB_OFFSET_N_SAMPLES")
#endif


#define NB_RAW_VALUE_BIT_SHIFT		5	// raw ADC values are shifted by 5 (divided by 32) when getting sent via sigfox.

typedef struct nestboxEvent {
	uint32_t start_timestamp;
	uint32_t stop_timestamp;

	uint64_t rfid_uid;

	unsigned int n_samples;

	int32_t raw_samples[NB_EVENT_N_SAMPLES];		// mean value from AC_pos and AC_neg
	int32_t ac_pos_samples[NB_EVENT_N_SAMPLES];
	int32_t ac_neg_samples[NB_EVENT_N_SAMPLES];

	int32_t stddev;
	int32_t raw_mean;
	int32_t raw_median;
	int32_t ac_pos_median; // from same sample index like raw_median
	int32_t ac_neg_median; // from same sample index like raw_median

	float weight_estimate;	// in grams
	float stddev_estimate;	// in grams

	uint8_t flags;
	float temperature;
} nestbox_event_t;

// event functions:
void nestbox_request_cli_process();
void nestbox_request_usb_state_change();
void nestbox_request_complete_startup();

void nestbox_main();

#endif /* INC_NESTBOX_H_ */

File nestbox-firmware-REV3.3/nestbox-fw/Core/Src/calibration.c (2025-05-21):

/*
 * calibration.c
 *
 *  Created on: 1 Oct 2021
 *      Author: raffael.tschui
 */

#include "calibration.h"
#include <stddef.h>
#include <math.h>
#include <string.h>
#include "rtc.h"
#include "../statistics/statistics.h"
#include "log.h"
#include "load_cell.h"

static load_cell_calib_t calib;

const float calib_weights[NB_N_CALIBRATION_WEIGHTS] = NB_DEFAULT_CALIBRATION_WEIGHTS;
const float calib_tolerances[NB_N_CALIBRATION_WEIGHTS] = NB_CALIBRATION_WEIGHTS_TOLERANCES;
static nestbox_event_t calib_events[NB_N_CALIBRATION_WEIGHTS];
static char calib_events_available[NB_N_CALIBRATION_WEIGHTS] = {0,0,0,0};

static unsigned char calib_event_state = CALIB_NO_WEIGHT_ON_PERCH;

static void calib_apply(float new_slope, int32_t new_intercept, float r2, float temperature, struct calib_info_struct info);

float calib_get_slope(){
	return calib.slope;
}

int32_t calib_get_detection_threshold()
{
	return calib.detection_threshold;
}

int32_t calib_get_stdev_max_valid()
{
	return calib.stdev_max_valid;
}

int32_t calib_get_max_sample_diff_valid()
{
	return calib.sample_diff_max_valid;
}


uint8_t calib_get_id()
{
	return calib.info.id;
}

int calib_add_event(nestbox_event_t* evt)
{
	// identify weight:

	for(int i=0; i<NB_N_CALIBRATION_WEIGHTS; i++)
	{

		if(calib_weights[i] - calib_tolerances[i] < evt->weight_estimate &&
				calib_weights[i] + calib_tolerances[i] > evt->weight_estimate)
		{
			// the weight was identified --> store it:
			memcpy(&calib_events[i], evt, sizeof(calib_events[i]));
			calib_events_available[i] = 1;
			return CALIB_OK;
		}
	}

	return CALIB_ERROR;
}

int calib_new_ongoing()
{
	int ongoing = 0;

	if(calib_events_available[0] > 0)
		ongoing = 1;
	if(calib_events_available[1] > 0)
		ongoing = 1;

	#if(NB_N_CALIBRATION_WEIGHTS > 2)
		if(calib_events_available[2] > 0)
			ongoing = 1;
	#endif
	#if(NB_N_CALIBRATION_WEIGHTS > 3)
		if(calib_events_available[3] > 0)
			ongoing = 1;
	#endif


	return ongoing;
}

void calib_reset_ongoing()
{
	calib_events_available[0] = 0;
	calib_events_available[1] = 0;
#if(NB_N_CALIBRATION_WEIGHTS > 2)
	calib_events_available[2] = 0;
#endif
#if(NB_N_CALIBRATION_WEIGHTS > 3)
	calib_events_available[3] = 0;
#endif
}

void calib_inform_weight_removed()
{
	calib_event_state = CALIB_NO_WEIGHT_ON_PERCH;
}

void calib_inform_weight_detected()
{
	calib_event_state = CALIB_WEIGHT_DETECTED; // before RFID detection (if not in calib mode)
}

void calib_inform_weight_measurement_ongoing()
{
	calib_event_state = CALIB_WEIGHT_MEASUREMENT_ONGOING; // after RFID detection (if not in calib mode)
}

void calib_inform_weight_measurement_completed()
{
	calib_event_state = CALIB_WEIGHT_MEASUREMENT_COMPLETED;
}



// Conclude calibration:
int calib_process_events()
{
	double x[NB_N_CALIBRATION_WEIGHTS];
	double y[NB_N_CALIBRATION_WEIGHTS];
	float average_temperature = 0.0;

	int n_events = 0;

	for(int i=0; i<NB_N_CALIBRATION_WEIGHTS; i++)
	{
		if(calib_events_available[i] == 1)
		{
			x[n_events] = calib_weights[i];
			y[n_events] = calib_events[i].raw_median;
			average_temperature += calib_events[i].temperature;
			n_events++;
		}
	}

	if(n_events < NB_N_MINIMUM_CALIBRATION_WEIGHTS)
	{
		return CALIB_ERROR;
	}


	average_temperature = average_temperature/n_events;

	// gather calibration info:
	struct calib_info_struct new_calib_info;
	new_calib_info.id = (calib.info.id + 1) % COMM_N_CALIB_IDS;
	new_calib_info.used_w1 = (calib_events_available[0] > 0);
	new_calib_info.used_w2 = (calib_events_available[1] > 0);
#if(NB_N_CALIBRATION_WEIGHTS > 2)
	new_calib_info.used_w3 = (calib_events_available[2] > 0);
#else
	new_calib_info.used_w3 = 0;
#endif
#if(NB_N_CALIBRATION_WEIGHTS > 3)
	new_calib_info.used_w4 = (calib_events_available[3] > 0);
#else
	new_calib_info.used_w4 = 0;
#endif

	// compute linear regression:
	double new_slope, new_intercept, r2;

	r2 = linear_regression(x, y, n_events, &new_slope, &new_intercept);

	if(r2 > NB_LINREG_MIN_R2 && r2<1.0)
	{
		calib_apply(new_slope, round(new_intercept), r2, average_temperature, new_calib_info);

		unsigned int i = 0;
		for(i = 0; i<NB_N_CALIBRATION_WEIGHTS; i++)
		{
			calib_events_available[i] = 0;
		}
		return CALIB_OK;
	}

	return CALIB_ERROR;
}


//void linregtest()
//{
//	double x[NB_N_CALIBRATION_WEIGHTS];
//	double y[NB_N_CALIBRATION_WEIGHTS];
//
//	int n_events = 0;
//
//	for(int i=0; i<NB_N_CALIBRATION_WEIGHTS; i++)
//	{
//			x[n_events] = i;
//			y[n_events] = i*3+4;
//			n_events++;
//	}
//
//	x[0] += 0.1;
//
//	// compute linear regression:
//
//	double new_slope, new_intercept, r2;
//
//	r2 = linear_regression(x, y, n_events, &new_slope, &new_intercept);
//
//	if(r2 > NB_LINREG_MIN_R2 && r2<1.0)
//	{
//		struct calib_info_struct a;
//		calib_apply(new_slope, round(new_intercept), r2, 2, a);
//	}
//}


static void calib_apply(float new_slope, int32_t new_intercept, float r2, float temperature, struct calib_info_struct info)
{
	calib.timestamp = rtc_get_timestamp();
	calib.slope = new_slope;
	calib.intercept = new_intercept;
	calib.r2 = r2;
	calib.temperature = temperature;

	calib.detection_threshold = new_slope * NB_DETECTION_THRESHOLD;
	calib.overload_threshold = new_slope * NB_OVERLOAD_THRESHOLD;
	calib.stdev_max_valid = new_slope * NB_MAX_STDEV_FOR_VALID_SAMPLE;
	calib.sample_diff_max_valid = new_slope * NB_MAX_DIFF_FOR_VALID_SAMPLE;

	calib.info = info;
}

int calib_pack_message(comm_calib_t* clb)
{
	clb->info = calib.info;
	clb->slope = round(calib.slope * 100.0);
	clb->intercept = calib.intercept >> NB_RAW_VALUE_BIT_SHIFT; // shifted by 5 bits
	clb->temperature = round(calib.temperature*100.0);
	clb->r2 = calib.r2;

	return 0;
}

void calib_backup()
{
	GD5F1GQ4_write_backup_register(LOG_BKP_REG_CALIB_SLOPE, *(uint32_t*)(&calib.slope));
	GD5F1GQ4_write_backup_register(LOG_BKP_REG_CALIB_INTERCEPT, calib.intercept);
	GD5F1GQ4_write_backup_register(LOG_BKP_REG_CALIB_R2, *(uint32_t*)&calib.r2);
	GD5F1GQ4_write_backup_register(LOG_BKP_REG_CALIB_TEMP, *(uint32_t*)&calib.temperature);
	GD5F1GQ4_write_backup_register(LOG_BKP_REG_CALIB_INFO, *((uint8_t*)&(calib.info)));
	GD5F1GQ4_write_backup_register(LOG_BKP_REG_CALIB_TIME, (uint32_t)calib.timestamp);
	GD5F1GQ4_write_backup_register(LOG_BKP_REG_CALIB_PW, (uint32_t)CALIB_BACKUP_PW);

}
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

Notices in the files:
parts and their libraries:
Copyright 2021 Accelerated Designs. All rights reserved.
